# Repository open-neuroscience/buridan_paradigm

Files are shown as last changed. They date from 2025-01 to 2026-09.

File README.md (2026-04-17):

# Buridan paradigm

This project has created open source hardware to perform experiments in a "Buridan paradigm"

First described in 1980 by Goetz [reference](https://pubmed.ncbi.nlm.nih.gov/6779803/) in a visual discrimination context for Drosophila melanogaster, the Buridan Paradigm follows from "buridan's ass" where a hypotetical donkey would die of starvation and thirst if placed at the same distance from a water and a food source, being equally thirsty and hungry. For the experiment using Drosophila, an animal without flying capabilities is placed in an arena, where it is free to walk. Outside of the arena, visual stimuli can be presented, and the movement of the animal towards, or away from these stimuli are recorded and measured.

This implementation of this paradigm relies on commercially available RGB LED Matrices (64x64 leds, with 3mm pitch) and the excellent control library https://github.com/hzeller/rpi-rgb-led-matrix. The system is controlled by a raspberry pi, and it is mechanically put together with Makerbeams, 3D printed parts, screws and nuts. An USB ELP Camera records the fly movement from above. Software was developed in collaboration with [BFKLAB](https://www.bfklab.com/)

Currently (Jan 2026) the system is being tested in the laboratory of [Prof. Sugie](https://www.bri.niigata-u.ac.jp/~neuroscience_disease_sugie/lab/en/) at the Niigata University in Japan 

Researchers and enthusiasts interested in replicating the system can get in touch with [Andre](andremchagas@proton.me)

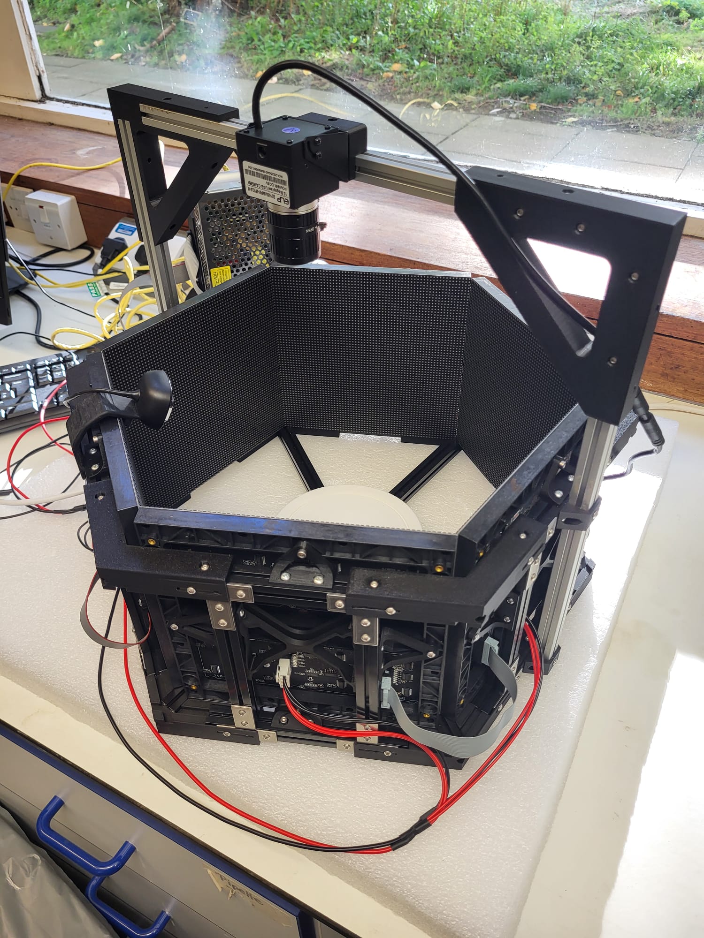
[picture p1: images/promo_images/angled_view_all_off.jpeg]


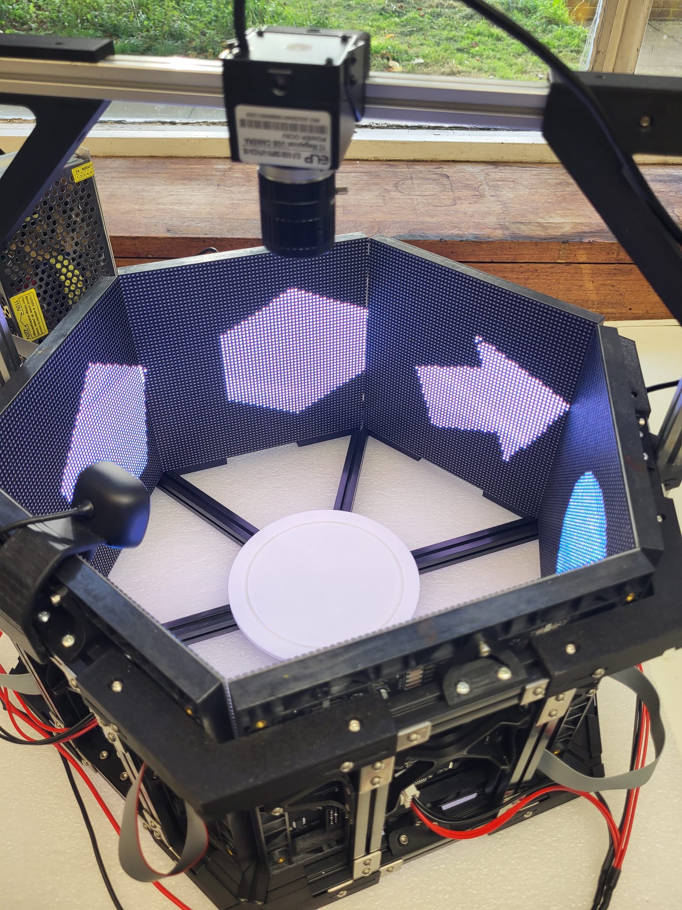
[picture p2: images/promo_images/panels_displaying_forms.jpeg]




---

### Academic references

- https://pubmed.ncbi.nlm.nih.gov/6779803/ - Visual Guidance in Drosophila

### Related hardware components, software, etc

#### LED panels:

- https://elifesciences.org/articles/63355
- https://www.sciencedirect.com/science/article/pii/S096098220800167X
- https://reiserlab.github.io/Modular-LED-Display/

#### Webcams:

- ELP non-IR (high frame rate - up to 250): https://www.amazon.co.uk/ELP-5-50mm-Computer-Comference-Raspberry/dp/B08Y5SG1BF/
- ELP IR: (frame rate up to 60): https://www.amazon.co.uk/ELP-KL36IR-Webcam-Infrared-Camera/dp/B07G56VVYR

#### supporting frames:

- MakerbeamXL: https://www.makerbeam.com/makerbeamxl/

#### RGB matrix driving systems:

- https://github.com/hzeller/rpi-rgb-led-matrix
- https://learn.lushaylabs.com/led-panel-hub75/

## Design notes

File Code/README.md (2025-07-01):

## Install the library
1. Enable ssh
2. Make sure to update rpi
3. ssh from computer (user@)
4. `git clone https://github.com/hzeller/rpi-rgb-led-matrix/`
5. `cd rpi-rgb-led/`
6. `cd lib/`
7. `make`
8. `cd ..`
9. `make` (root rpi led folder)
## Disable sound snd_bcm2835
1. `cd /etc/modprobe.d`
2. `sudo nano alsa-blacklist.conf`
3. type/ add 'blacklist snd_bcm2835'
4. exit nano (ctrl+X,Y)
5. `sudo reboot`
(As seen [here](https://www.instructables.com/Disable-the-Built-in-Sound-Card-of-Raspberry-Pi/))

## Use the demo
1. `cd rpi-rgb-led-matrix/examples-api-use`
2. `./demo -D 1 runtext.ppm`
3. Ctrl+C to quit
4. `./demo help` to explore what else you can do
5. `sudo ./demo --led-rows=64 --led-cols=64 --led-chain=2 --led-parallel=3 --led-slowdown-gpio=4 --led-pixel-mapper="U-mapper;rotate:90" -D1 runtext.ppm` is a good example of what the closest thing to working
## Using the custom pixel mapper
In an attempt to maximise frame-rate, we wanted to use 3 parallel chains of 2 rather than 1 chain of 6. The custom pixel mapper allows the 3 parallel chains of 2 in the setup to behave as one long continuous banner. See the example at the end of this doc - since the screens are upside-down they still require a 180 degree rotation.
#### Make Files:
1. `nano lib/horizontal_mapper.cc`
2. copy-paste the contents of horizontal_mapper.cc from this repo
3. `nano lib/horizontal_mapper.h`
4. copy-paste the contents of the `horizontal_mapper.h` file in this repo
#### Update Existing Files:
1.  `nano lib/pixel-mapper.cc`
2.  At the top of the file, add the following, after the includes:
	> #include "horizontal_mapper.h" 
3.  Find the `CreateMapperMap()` function
4.  After the lines that say `RegisterPixelMapperInternal(....)`, add the following (BEFORE `return result;`):
	> RegisterPixelMapperInternal(result, new HorizontalMapper());
5.  Save and quit the file
	* For nano, this is Ctrl+X
6. `nano lib/Makefile`
7.  Near the top of the file there is a line(s) that starts: `OBJECTS = file1.o file2.o etc...`
8. Add `horizontal_mapper.o` after the last `.o` string
	* Note that there may be multiple lines, separated by a `\` - this is fine, just add to the end of the last .o line
9. Save and quit the file
#### Remake
1. `cd lib/`
2. `make`
3. `cd ..`
4. `make`
#### Example use in examples-api-use/:
`sudo ./demo --led-rows=64 --led-cols=64 --led-chain=2 --led-parallel=3 --led-slowdown-gpio=4 --led-pixel-mapper="horizontal_mapper;rotate:180" --led-pwm-lsb-nanoseconds=50 --led-pwm-bits=8 -D1 runtext.ppm`
This example does a few things that a user may find useful:
1. Uses the custom pixel mapper with 180 degree rotation
2. Sets the pulse-length to 50 nanoseconds (the minimum value) to help with fps
3. Sets the bit-depth to 8 - decreasing the range of colours available (from 11-bit) but increases frame rate. Minimum value is 1 for very high fps
4. Displays refresh rate

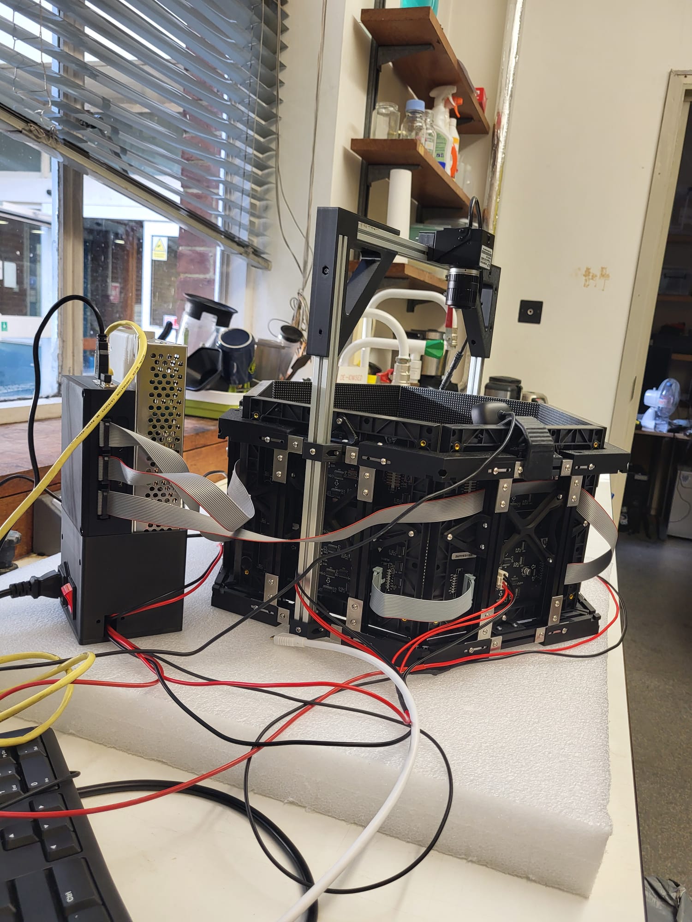
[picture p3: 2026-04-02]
images/promo_images/side_view_with_power_supply.jpeg

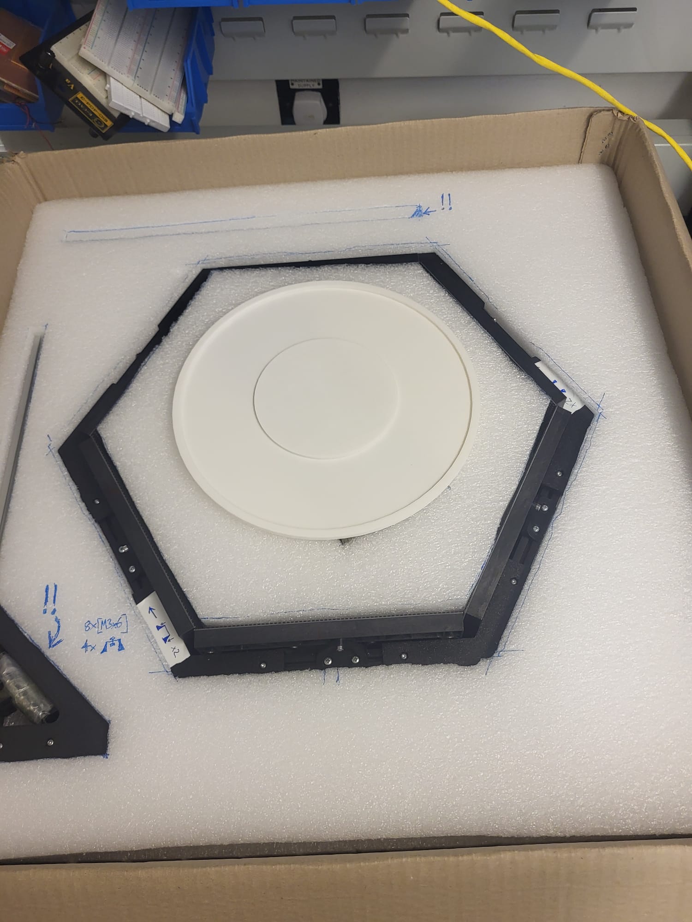
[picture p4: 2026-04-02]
images/promo_images/packaged.jpeg

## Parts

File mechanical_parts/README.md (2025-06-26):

Credit for X-brace design: https://www.printables.com/model/739917-beamcase-x-braces

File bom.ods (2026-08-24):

why | qty | link | unit cost (BRL+shipping) | total cost | obs | cost for parts currently in BRL | total cost
print base where flies will be | 2 | https://www.mercadolivre.com.br/filamento-petg-hf-preto-1kg-impressao-fabricacao-nacional-voolt3d/p/MLB31002299 | 150 | 300 |  | 5946,1 | 7096,1
control visual stimuli | 1 | https://www.mercadolivre.com.br/kit-raspberry-pi4-pi-4-model-b-4gb-ram-novo-nota-fiscal/p/MLB2038781731 | 1200 | 1200 | kit here
power RPI4 | 1 |  |  | 0 | in the kit above
operating system on RPI4 | 1 | https://www.mercadolivre.com.br/cartao-de-memoria-sandisk-ultra-100mbs-32gb-pcameras-wifi/up/MLBU3914236520 | 200 | 200 | in the kit above
connect RPI to computer screen | 1 |  |  | 0 | in the kit above
control raspberry pi for development | 1 | https://www.mercadolivre.com.br/teclado-e-mouse-sem-fio-dell-km3322w/p/MLB23368382 | 170 | 170
connect up to 3 streams of matrices | 1 | https://www.electrodragon.com/product/rgb-matrix-panel-drive-board-for-raspberry-pi-v2/ | 100 | 100
 | 1 | https://www.mercadolivre.com.br/camara-usb-elp-vision-fhd-1080p-angulo-infrarrojo-36-de-/p/MLB2027013675 | 500 | 500
visually stimulation for flies | 6 | https://www.mercadolivre.com.br/modulo-indoor-reposicao-placa-led-p3-64x64-19cm-x-19cm-v10/up/MLBU4214018776 | 250 | 1500
connect matrices to RPI4 | 6 |  |  | 0 | in the bundle above
power everything from one place | 1 | https://www.mercadolivre.com.br/fonte-chaveada-fgb-5v-30a-bivolt-com-protecao-de-curto-circuito/p/MLB38937589 | 120 | 120
 | 1 | https://www.mercadolivre.com.br/conector-painel-de-forca-c14-com-porta-fusivel-10-amperes/up/MLBU1733424013 | 20 | 20
 | 1 | https://www.mercadolivre.com.br/plus-do-brasil-cabo-de-forca-energia-10a-tripolar-p-pc-fonte-computador-cpu-monitor-eletronicos-c13-panela-eletrica-pressao-ro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 | 30 | 30
turn system on/off | 1 | https://www.mercadolivre.com.br/10-botao-liga-desliga-onoff-luminoso-kcd1-106n-escolher-acor/up/MLBU1407091830 | 2,9 | 2,9
hold things in place | 280 | https://www.mercadolivre.com.br/parafuso-cabeca-panela-ph-m3x6mm-zincado-jomarca-100un/p/MLB67849785 | 0,25 | 70
hold things in place | 280 | https://www.mercadolivre.com.br/porca-sextavada-m3-aco-inox-3mm-chave-55--100-pecas/up/MLBU764968165 | 0,19 | 53,2
arena construction | 2 | https://www.makerbeam.com/t-bracket-xl-black-anodised.html | 56 | 112
arena construction | 6 | https://www.makerbeam.com/150mm-4p-black-makerbeamxl-15mmx15mm.html | 50 | 300
arena construction | 2 | https://www.makerbeam.com/200mm-4p-black-makerbeamxl-15mmx15mm.html | 56 | 112
arena construction | 1 | https://www.makerbeam.com/300mm-4p-black-makerbeamxl-15mmx15mm.html | 77 | 77
import tax, shipping, etc | 1 |  | 1079 | 1079
(costs associated with energy, printer maintenance, etc) | 1 |  | 150 | 150
cost associated with building it | 5 |  | 200 | 1000

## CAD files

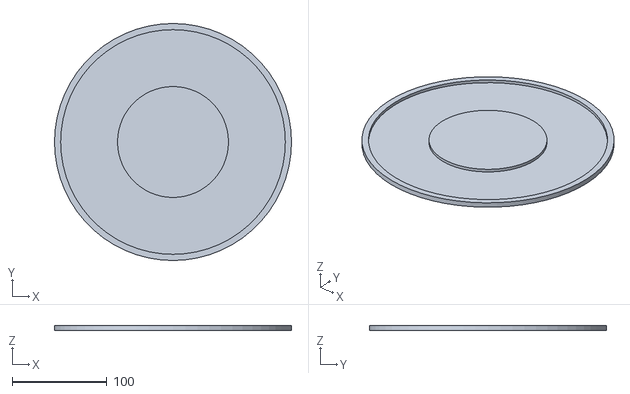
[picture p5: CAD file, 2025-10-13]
mechanical_parts/Arena Assembly 3D Print Parts/fly_base_250.stl
250.0 x 250.0 x 5.00

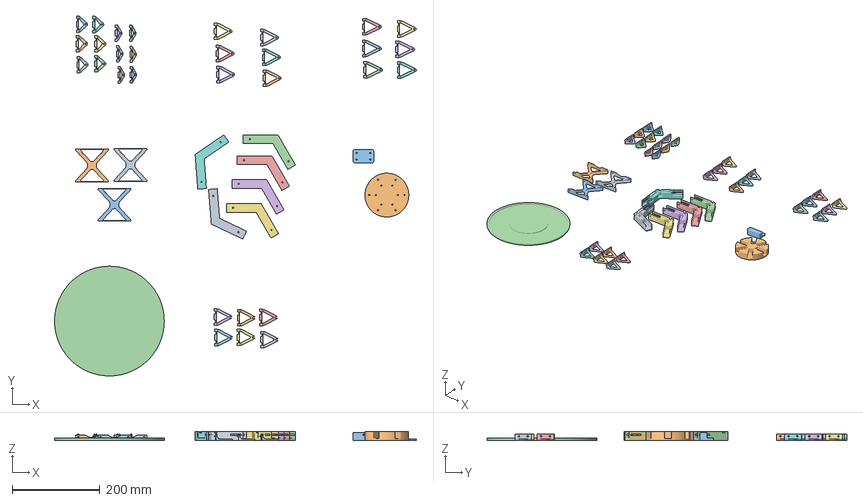
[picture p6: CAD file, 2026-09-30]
mechanical_parts/Electronics Enclosure 3D Print Parts/P1s/P1S_PLA_all_parts_buridan.3mf
824.1 x 819.5 x 20.0 mm
screen bracket_8.stl x 6
screen bracket_17.stl x 6
screen bracket_32.stl x 6
screen bracket_34.stl x 6
Frame X-brace 75x75mm.STL x 3
makerbeam-join.stl x 6
central_join.stl
camera_mount.stl
fly_base_250.stl
test_screen_bracket_32mm.stl x 6

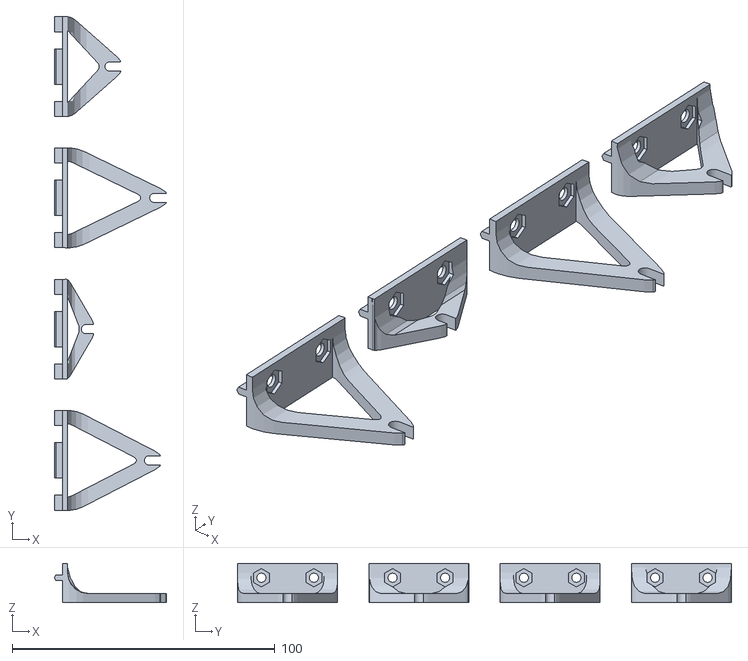
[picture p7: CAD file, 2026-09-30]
mechanical_parts/Electronics Enclosure 3D Print Parts/test_screen_brackets.stl
42.7 x 188.2 x 15.0

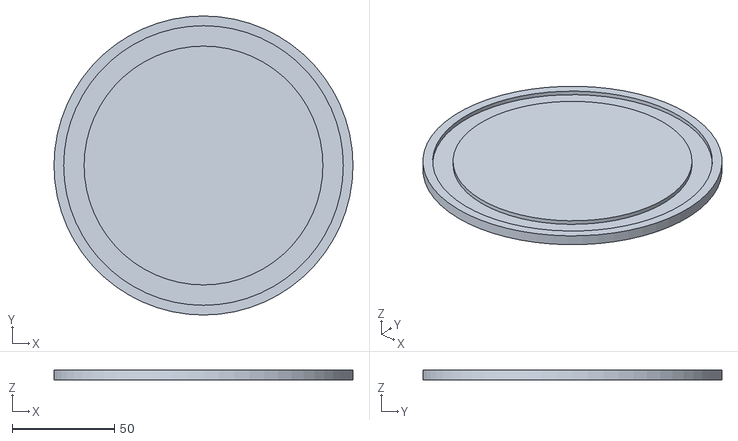
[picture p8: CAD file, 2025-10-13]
mechanical_parts/Arena Assembly 3D Print Parts/fly_base.stl
146.5 x 146.5 x 5.00

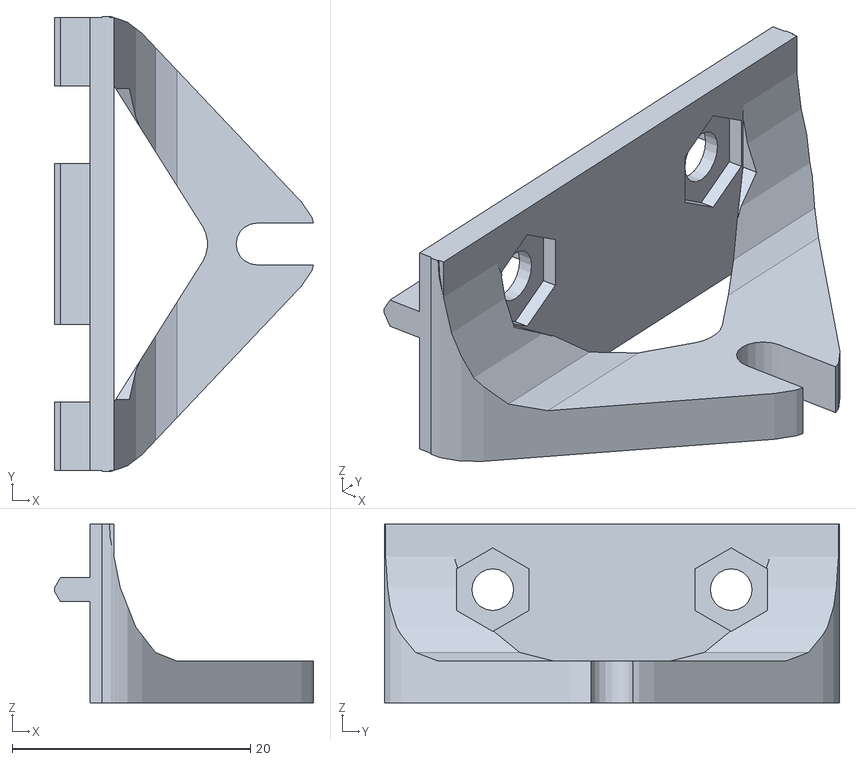
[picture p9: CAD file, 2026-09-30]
mechanical_parts/Electronics Enclosure 3D Print Parts/test_screen_bracket_13mm.stl
21.7 x 38.2 x 15.0

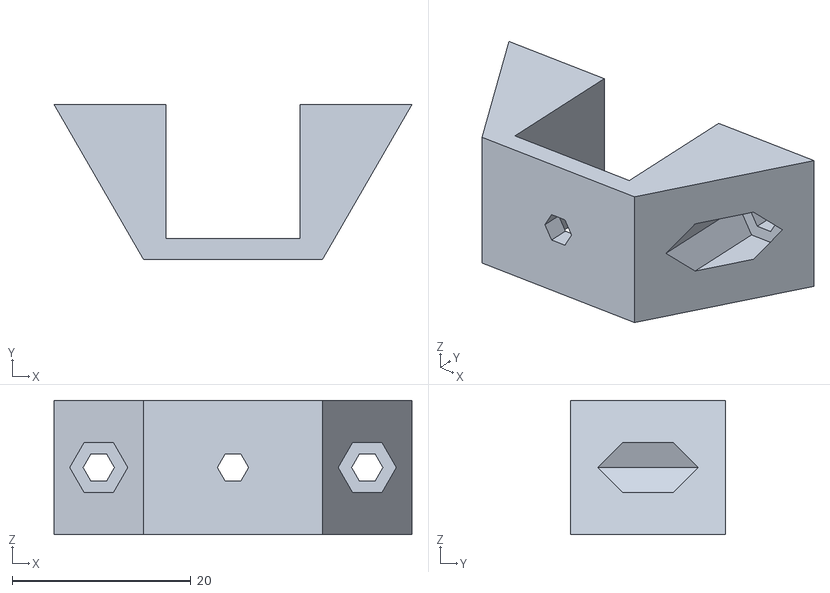
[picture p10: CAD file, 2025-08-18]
mechanical_parts/Arena Assembly 3D Print Parts/vertical beam mount.stl
40.0 x 17.3 x 15.0

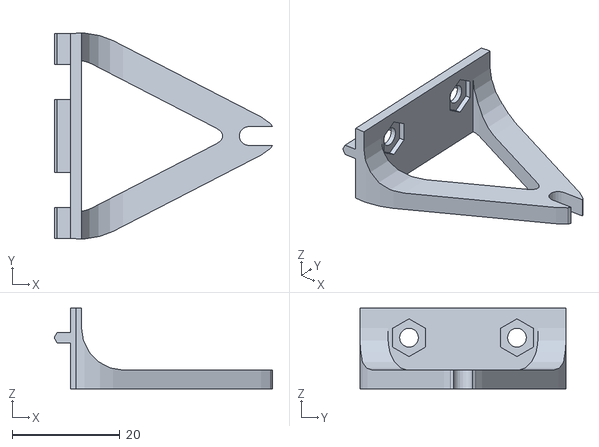
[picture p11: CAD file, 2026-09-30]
mechanical_parts/Electronics Enclosure 3D Print Parts/test_screen_bracket_32mm.stl
40.4 x 38.2 x 15.0

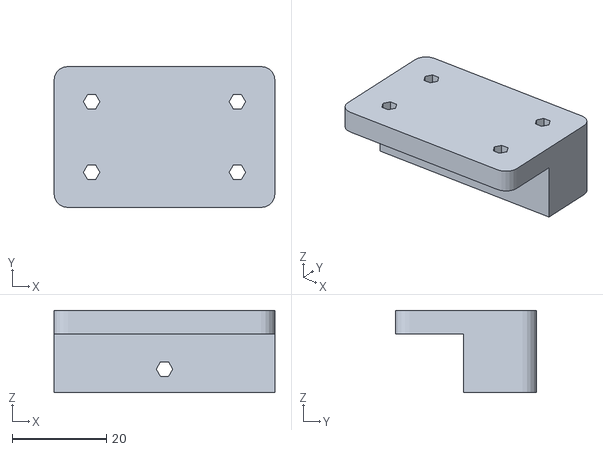
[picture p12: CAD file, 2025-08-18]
mechanical_parts/Arena Assembly 3D Print Parts/camera_mount.stl
47.0 x 30.0 x 17.5

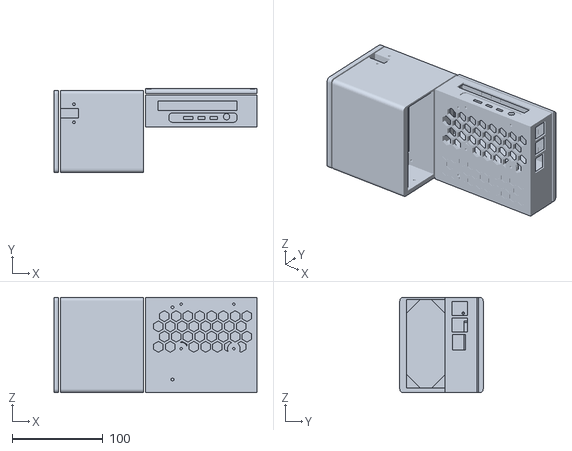
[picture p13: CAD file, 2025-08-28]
mechanical_parts/Electronics Enclosure 3D Print Parts/all_enclosures.stl
223.5 x 92.0 x 105.0

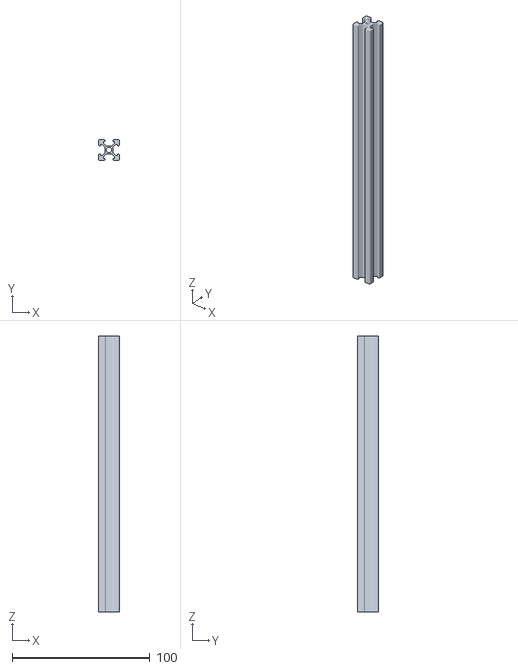
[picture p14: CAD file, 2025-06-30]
mechanical_parts/Arena Assembly 3D Print Parts/makerBeam_200mm.stl
15.0 x 15.0 x 200.0

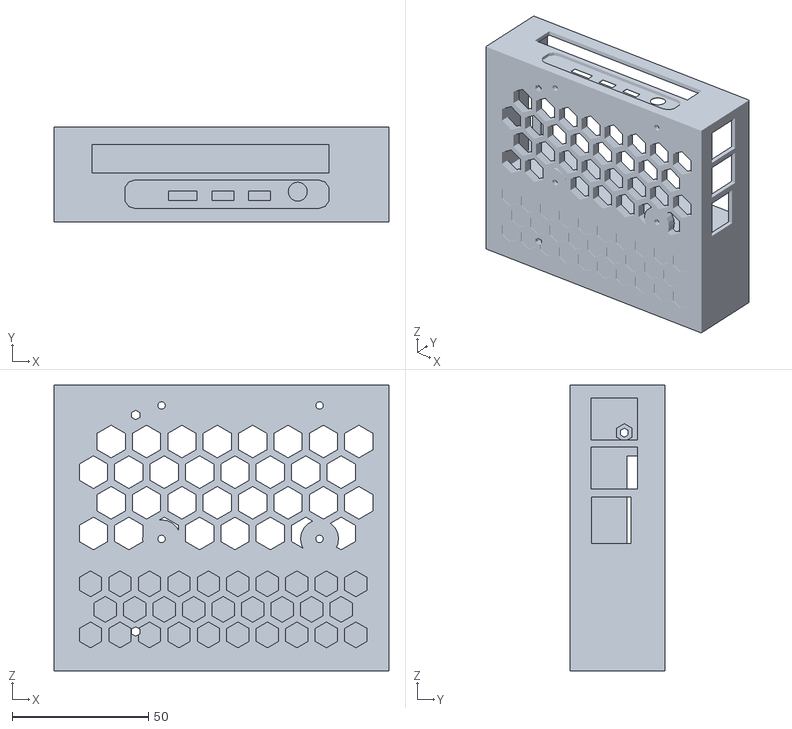
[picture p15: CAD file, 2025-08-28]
mechanical_parts/Electronics Enclosure 3D Print Parts/Enclosure.stl
123.0 x 35.0 x 105.0

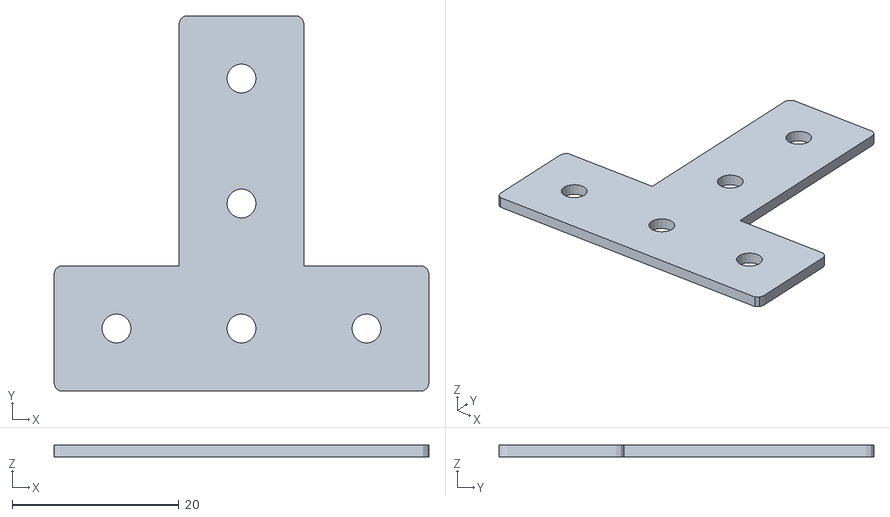
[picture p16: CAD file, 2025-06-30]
mechanical_parts/Arena Assembly 3D Print Parts/makerbeam_t-joint.stl
45.0 x 45.0 x 1.50

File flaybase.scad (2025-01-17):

//Buridan paradigm///
//fly plaform v0.1//
//CC BY SA 4.0 //
// first design by Andre Maia Chagas 17/01/2025//
//units in mm //

platD = 117;
platH = 5;
platEdgeD = 146.5;//platD+8;
tolerance = 0.1;
$fn=60;

//make platform
difference(){
cylinder(d=platEdgeD,h=platH,$fn=60);
translate([0,0,3]){
cylinder(d=platD+5,h=2.5);
}//end translate
}//end difference
cylinder(d=platD,h=platH);
%cylinder(d=platEdgeD+22.8,h=platH,$fn=6);

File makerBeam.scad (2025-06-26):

//Credit: https://www.thingiverse.com/thing:27825/files

$fn=50;

module makerBeam(length)
{
	difference(){
		union(){
			// body
			cube([8,8,length], center=true);
			// corners
			for (i=[0:3]){
				rotate([0, 0, i*90]){corner(length);}
			}
		}
		// center hole
		cylinder(h=length, r=2.5, center=true);
	};
}

module corner(length){
	difference(){
		union(){
			// arm
			rotate([0, 0, 45]){
				translate([0,5,0]){cube([1.4, 15, length], center=true);}
			}

			translate([-9, 7, 0]){cube([2, 6, length], center=true);}
			translate([-7, 9, 0]){cube([6, 2, length], center=true);}
			translate([-7, 7, 0]){cube([3, 3, length], center=true);}
		}

		translate([-4, 10, 0]){cylinder(h=length, r=0.5, center=true);}
		translate([-10, 4, 0]){cylinder(h=length, r=0.5, center=true);}

		// round external shape
		difference(){
			translate([-9.5, 9.5, 0]){cube([1, 1, length], center=true);}
			translate([-9, 9, 0]){cylinder(h=length, r=1, center=true);}
		}
	}
}


makerBeam(50);

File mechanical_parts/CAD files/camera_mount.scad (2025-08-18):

//camera mount

use <fillets_and_rounds.scad>

module camera_mount(){
    x_offset = 15.5;
    y_offset = 7.5;
    
    difference(){
    union(){
        add_rounds(axis="z",R=3,fn=20)cube([47,30,5],center=true);
        translate([0,0,-7.5])add_rounds(axis="z",R=3,fn=20)cube([47,30,15],center=true);
    }//end union
    for(i=[-1:2:1]){
        for(j = [-1:2:1]){
            translate([i*x_offset,j*y_offset,0])cylinder(d=3.5,h=50,center=true);
            //translate([i*x_offset,j*y_offset,-1])cylinder(d=6.5,h=3.5,$fn=6);
        }//end for
    }//end for
}
    
}//end module

module frame_mount(){
    difference(){
    translate([0,8,10])camera_mount();
    cube([60,15,15],center=true);
    rotate([90,0,0])cylinder(d=3.5,h=50,center=true);
        translate([0,15+5.5,0])rotate([90,0,0])cylinder(d=6.6,h=15,$fn=6,center=true);
    }//end difference
}//end frame_mount

frame_mount();

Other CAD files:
mechanical_parts/Electronics Enclosure 3D Print Parts/P1s/PETG_under_support_P1S.gcode.3mf
mechanical_parts/Electronics Enclosure 3D Print Parts/P1s/PETG_arena_structure_brackets_P1S.gcode.3mf
mechanical_parts/Electronics Enclosure 3D Print Parts/P1s/PETG_matrices_structure_brackets_P1S.gcode.3mf
mechanical_parts/Electronics Enclosure 3D Print Parts/P1s/PETG_electronic_enclosures_P1S.gcode.3mf
mechanical_parts/Electronics Enclosure 3D Print Parts/P1s/PETG_fly_arena_P1S.gcode.3mf
mechanical_parts/Electronics Enclosure 3D Print Parts/P1s/PETG_camera_structure_brackets_P1S.gcode.3mf
mechanical_parts/CAD files/Enclosure.scad
mechanical_parts/Arena Assembly 3D Print Parts/Frame X-brace 75x75mm.STL
mechanical_parts/Arena Assembly 3D Print Parts/M3 NUT.stl
mechanical_parts/Arena Assembly 3D Print Parts/M3x6.STL
mechanical_parts/Arena Assembly 3D Print Parts/central_join.stl
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

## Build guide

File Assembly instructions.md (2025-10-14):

## 1. 3D print all parts in this [folder](/mechanical_parts/) to the required part number:  
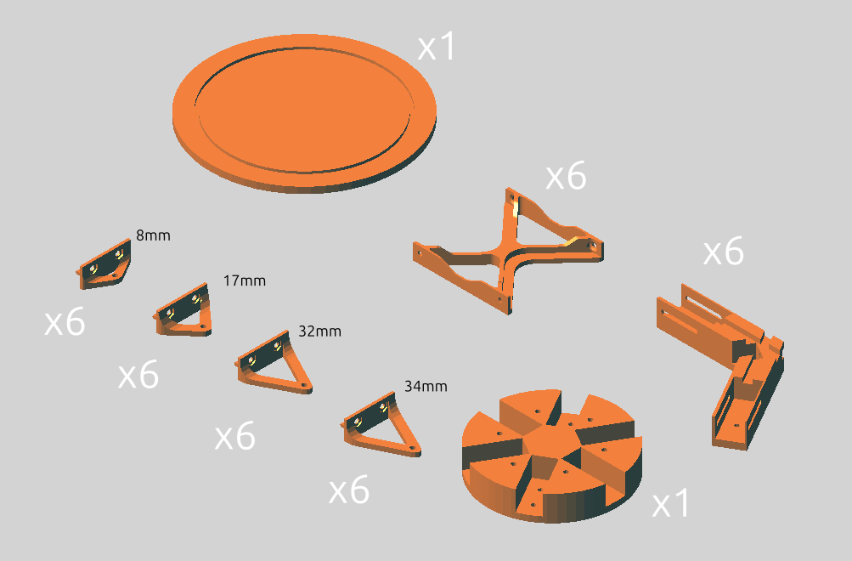
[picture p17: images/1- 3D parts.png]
   
## 2. Assemble 6 screen mounts:
1. Add 4 m3x6 screws and nuts to each (6) X-brace part:  
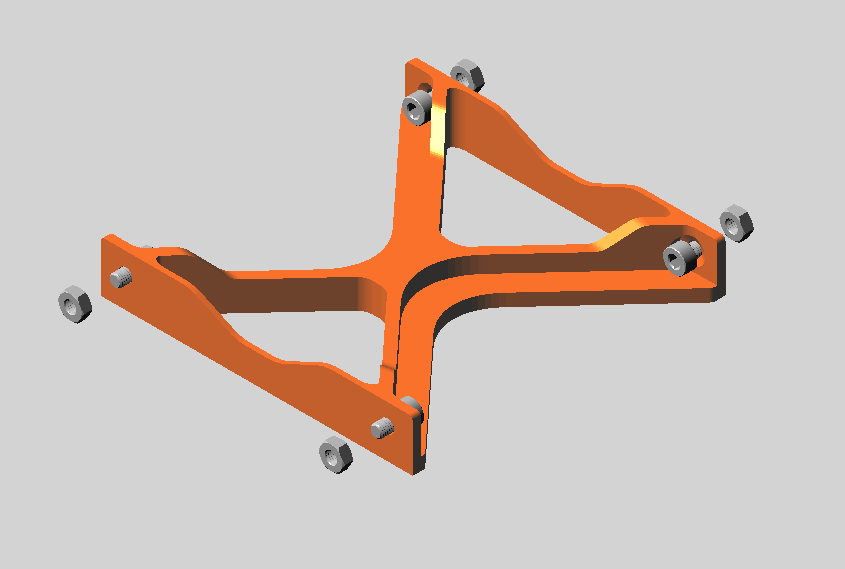
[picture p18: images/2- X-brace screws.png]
   
2. Slide makerbeamXL (150mm) on each side of each X-brace:  
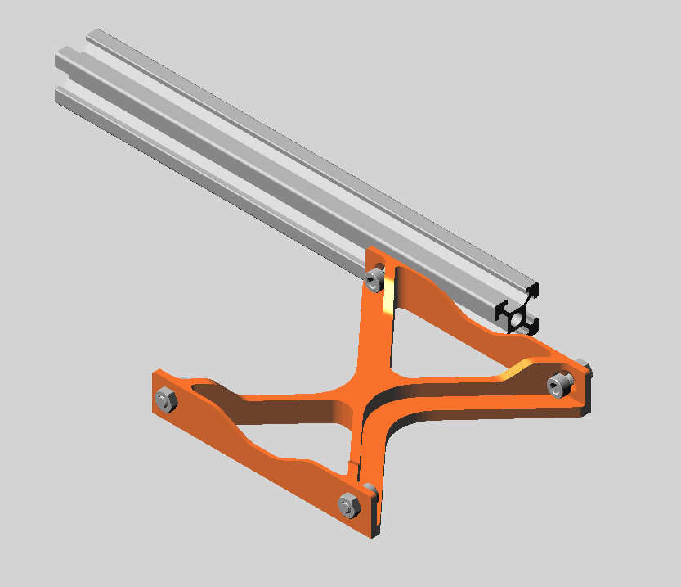
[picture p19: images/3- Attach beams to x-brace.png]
     
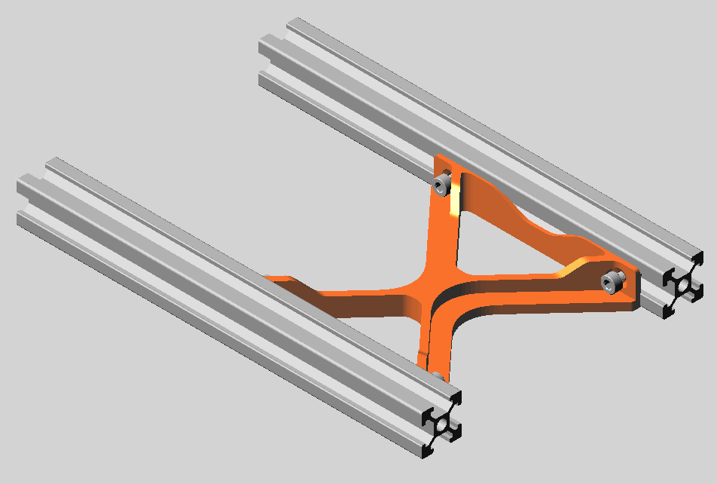
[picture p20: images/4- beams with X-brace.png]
     
3. Slide in 2 nuts to each side and screw on a printed 32mm (image left) and 34mm (image right) screen bracket to each side as shown:  
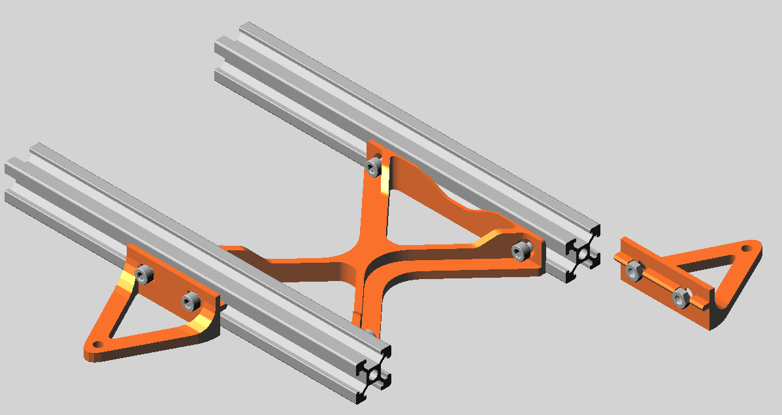
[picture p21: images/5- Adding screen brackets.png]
   
4. Attach screws and nuts to (12) t-plates and insert into the head of each unit as shown: (flipped)  
   _For TWO of these units, make sure to include two extra nuts between the T-plates_
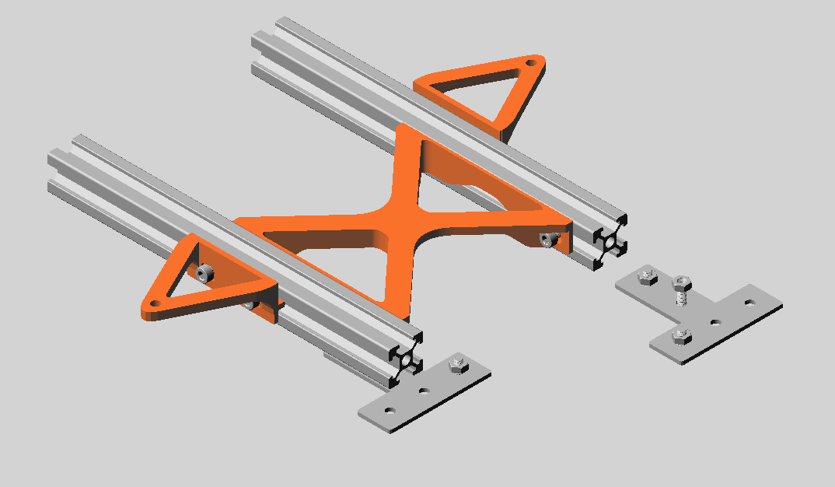
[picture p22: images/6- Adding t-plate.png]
   
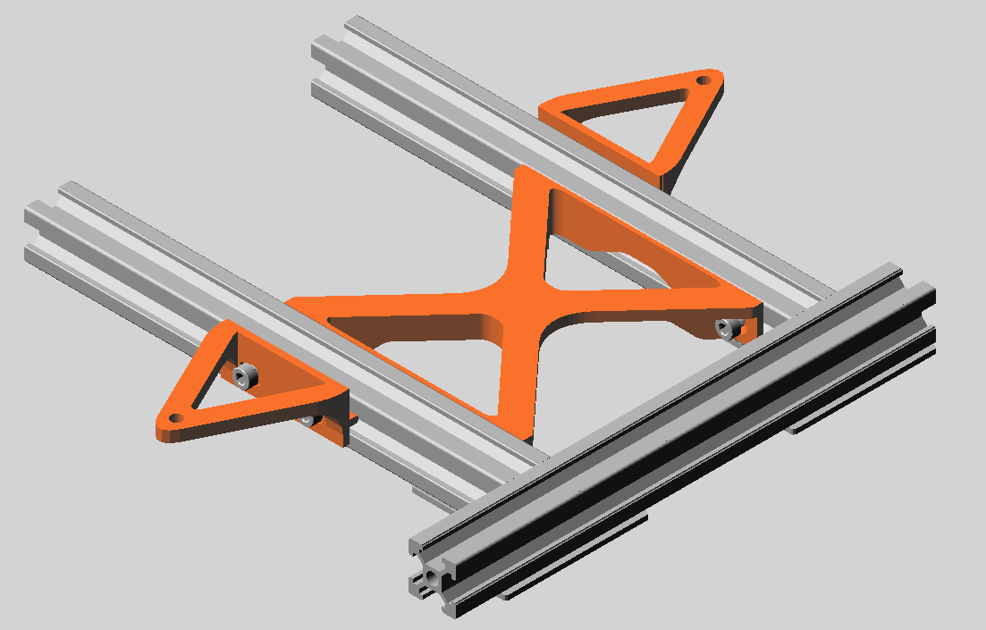
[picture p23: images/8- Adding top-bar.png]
5. Slide another 150mm makerbeamXL on to the top of the unit:    
6. Slide in two nuts and screw on the 17mm screen bracket:  
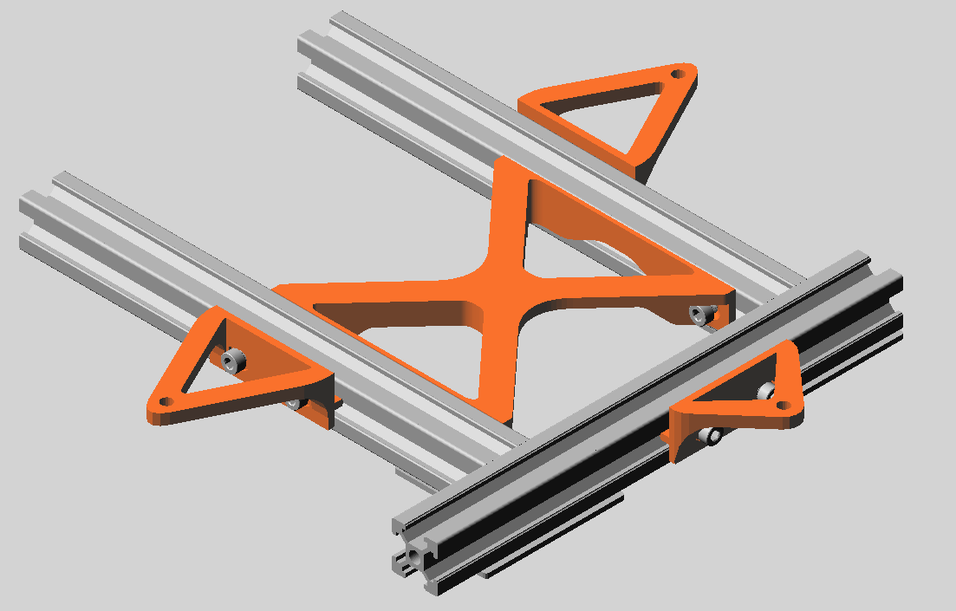
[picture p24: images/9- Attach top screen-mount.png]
     _Remember the extra nuts for two units_  
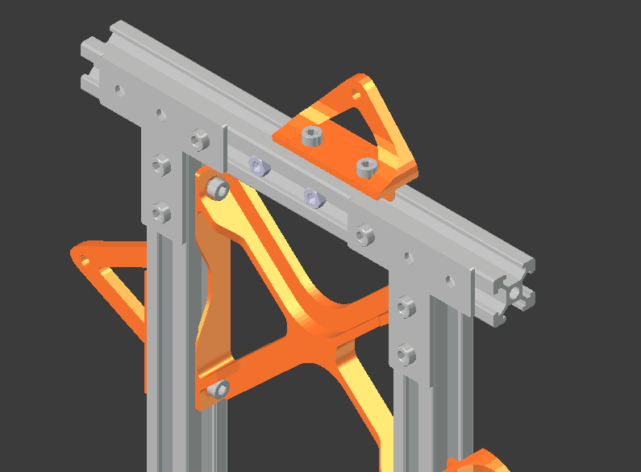
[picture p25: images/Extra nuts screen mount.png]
    
## 3. Assemble central hub
_Remember to glue in magnets to the top holes so they match those in the fly-base_
1. Add screws and nuts to the central hub object:  
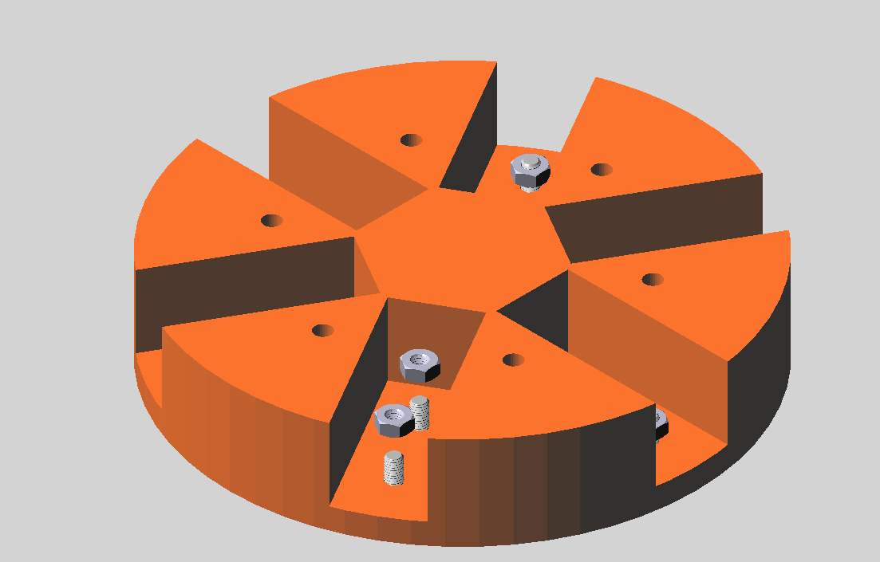
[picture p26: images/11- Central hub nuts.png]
     
2. Slide in six makerbeamXL 200mm beams:
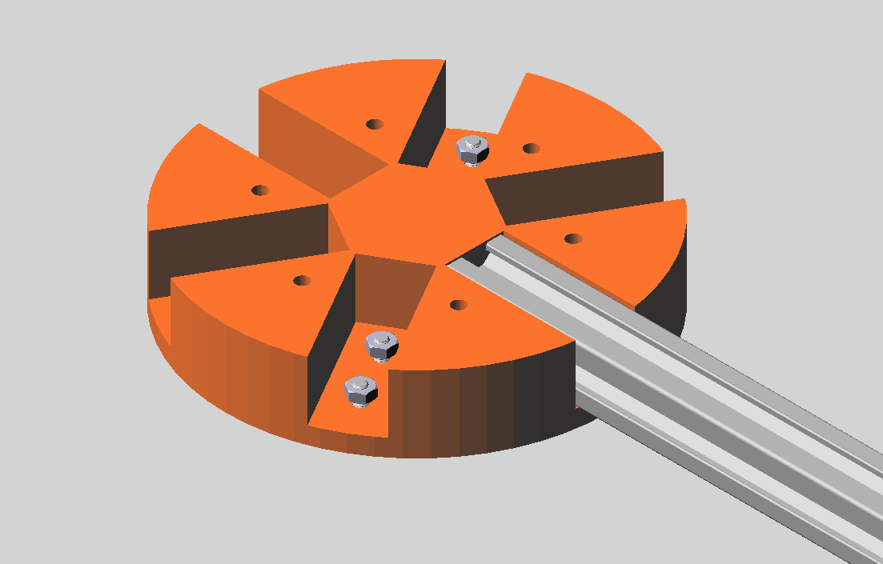
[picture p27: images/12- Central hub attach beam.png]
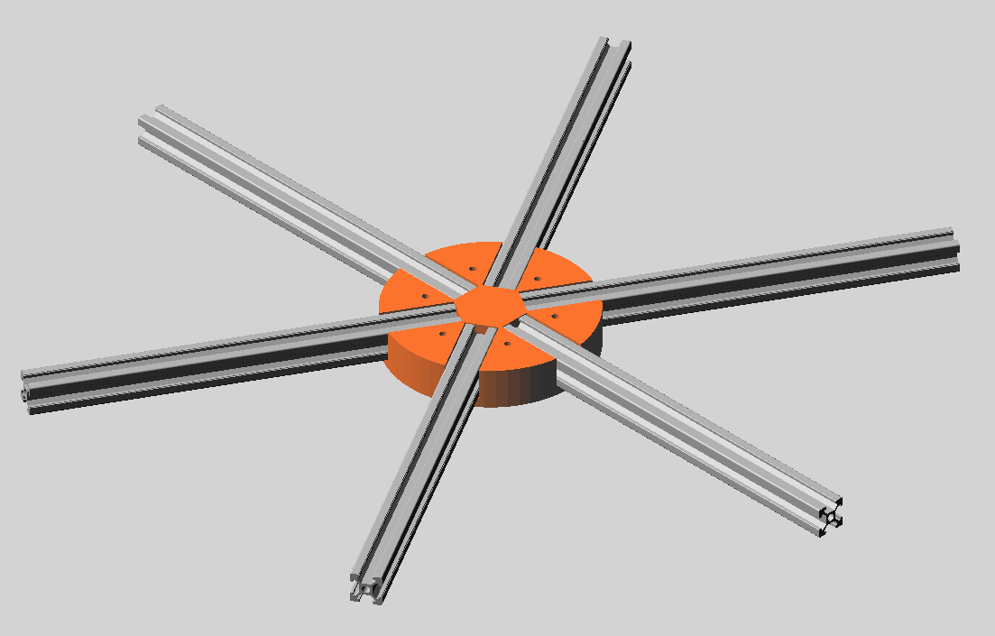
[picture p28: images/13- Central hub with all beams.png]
       
## 4. Assemble the Base
1.  Add screws and nuts to the corner join parts (x6):  
2. Attach a 150mm makerbeam and t-plate (x5): 
	_Don't forget the  nuts shown (left) for two units)
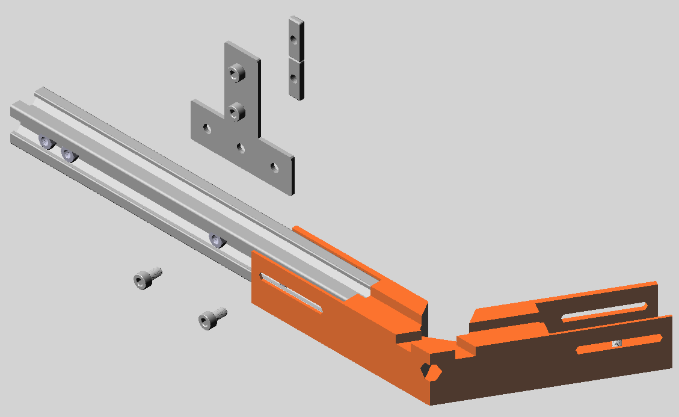
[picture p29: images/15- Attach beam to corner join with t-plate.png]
	
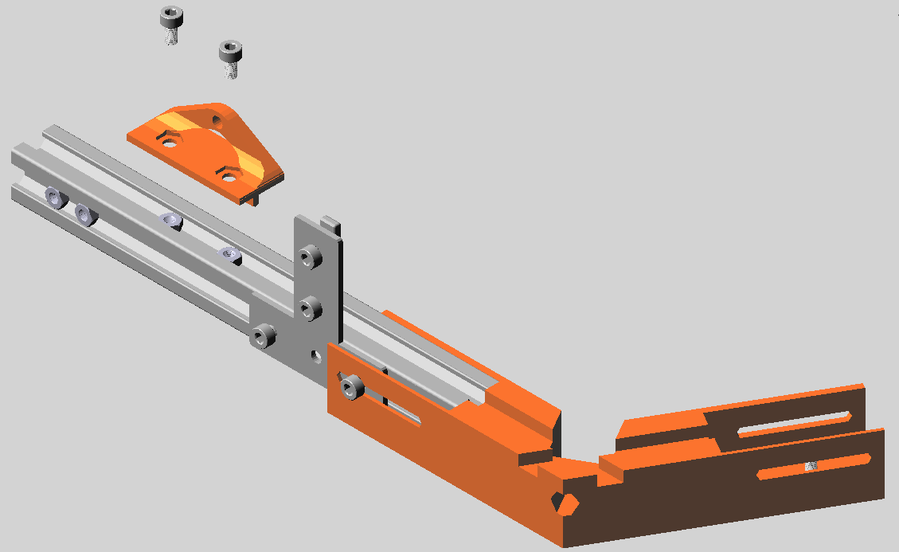
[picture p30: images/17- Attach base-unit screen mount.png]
3.  Add two more nuts to the top of the beam and attach the 8mm screen bracket: 
4.  Insert two extra nuts into TWO sections only:
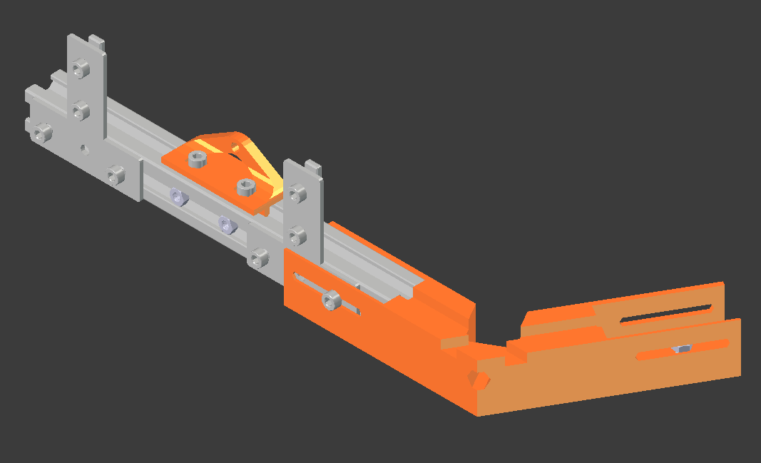
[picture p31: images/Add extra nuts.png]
	
5. Attach the remaining corner part and slot together as shown:
	_Make sure the two sections with extra nuts are OPPOSITE
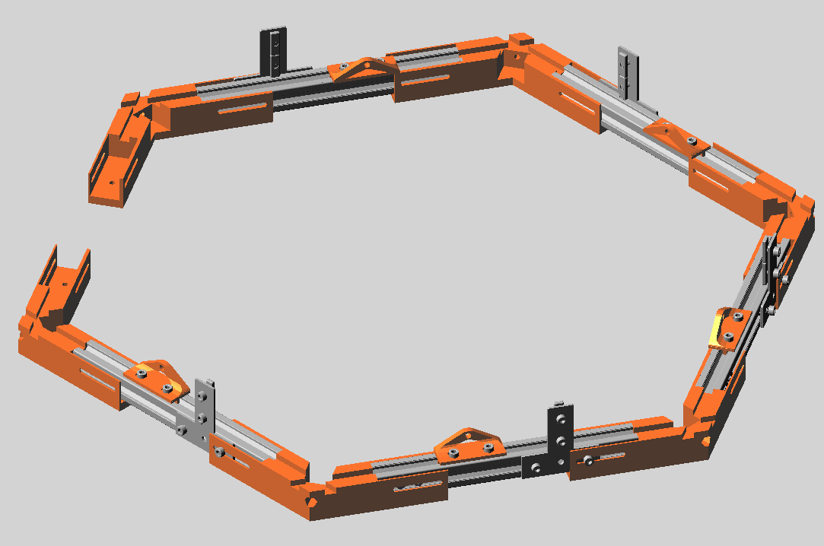
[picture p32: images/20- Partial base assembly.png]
	Note that these parts aren't yet screwed together_  
	
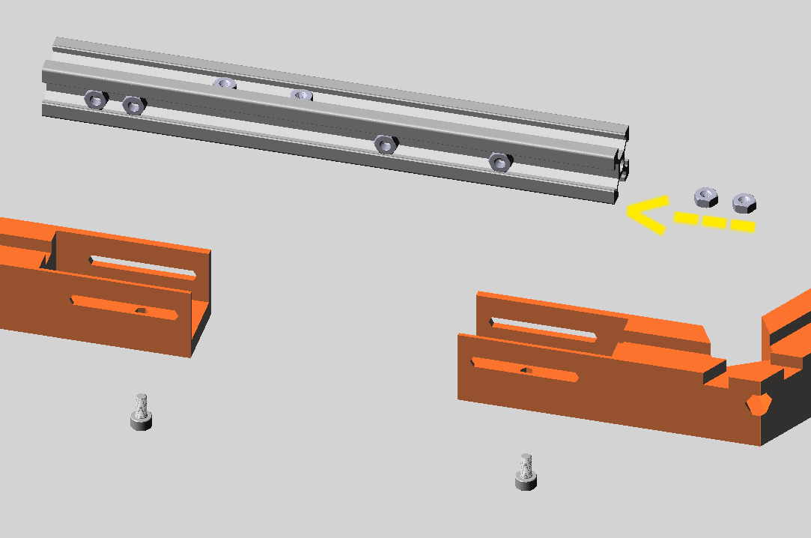
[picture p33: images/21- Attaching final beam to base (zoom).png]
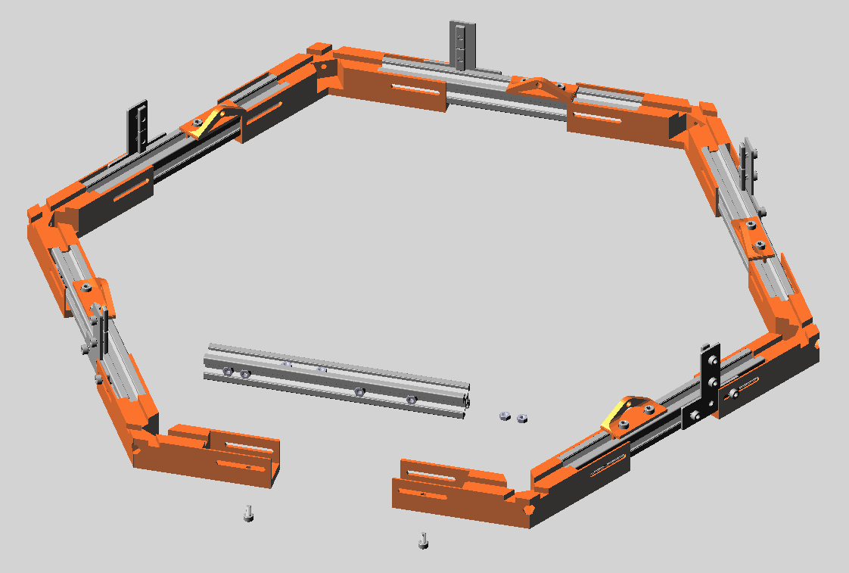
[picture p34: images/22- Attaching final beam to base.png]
6.  Attach the remaining beam with nuts as shown:   
7.  Attach remaining t-plates and screws: 
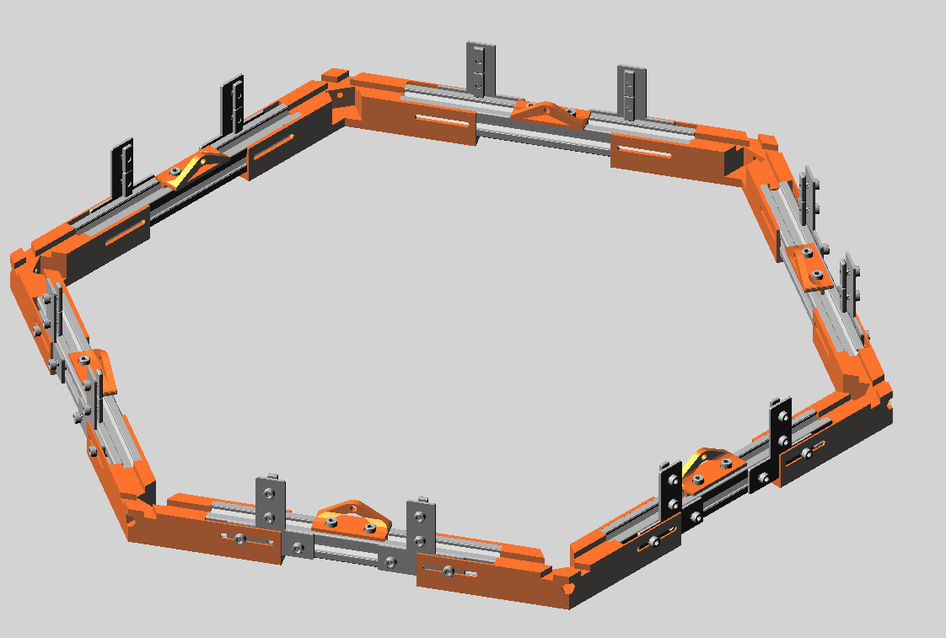
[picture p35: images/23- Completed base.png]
   _Note it's best to keep the screen mounts and t-plates loose enough to slide so they can be adjusted later_
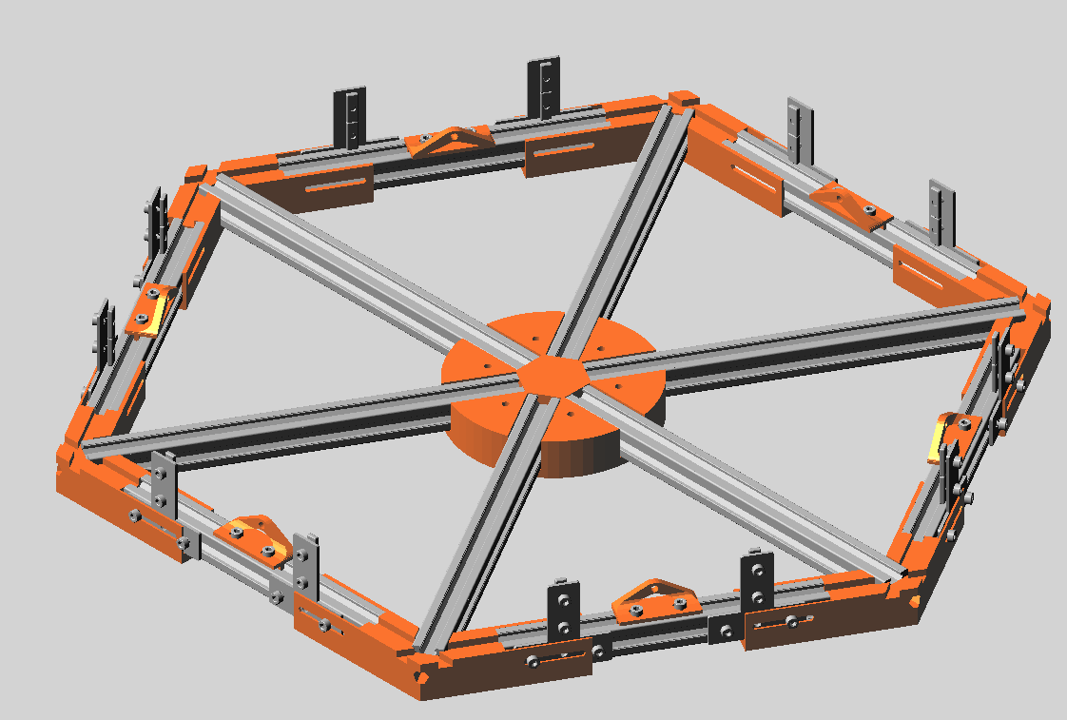
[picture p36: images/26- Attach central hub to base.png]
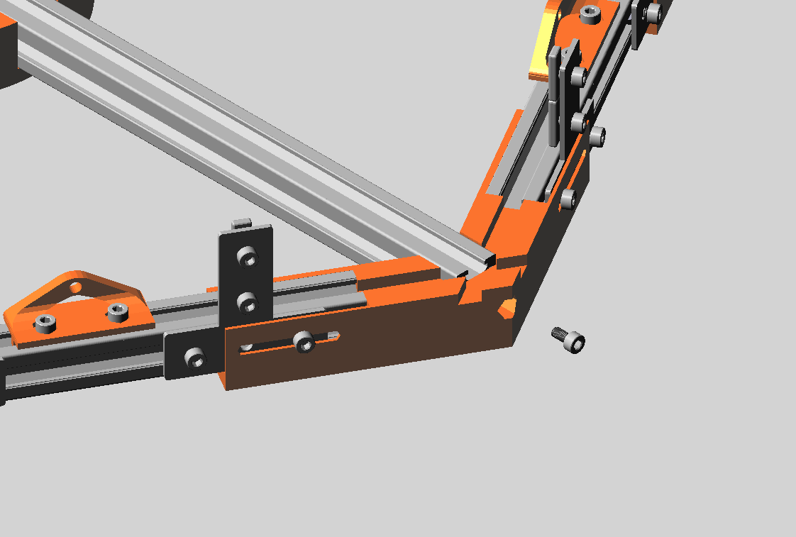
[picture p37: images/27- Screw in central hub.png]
8. Attach the central hub   
## 5. Finish the Frame
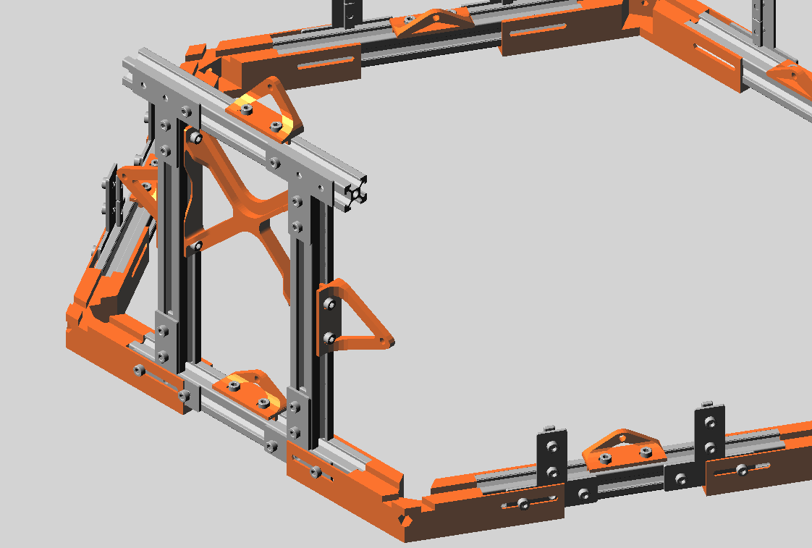
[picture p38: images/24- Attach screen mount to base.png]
1. Attach the screen mounts to the base  (x6)
2. Add nuts to the screen mount and attach the top
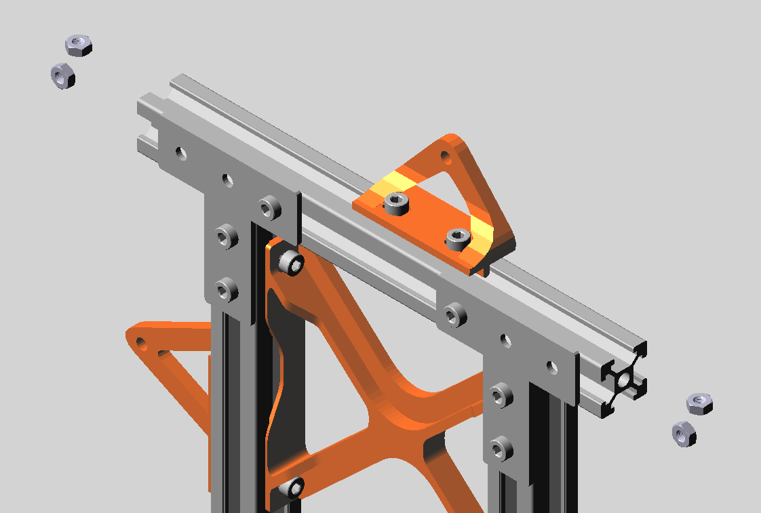
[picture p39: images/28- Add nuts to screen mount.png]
   
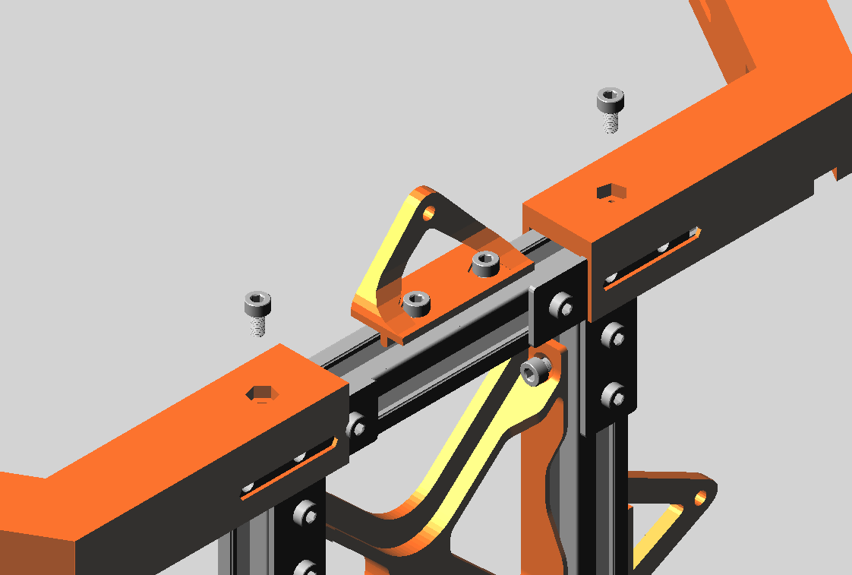
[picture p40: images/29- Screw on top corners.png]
   
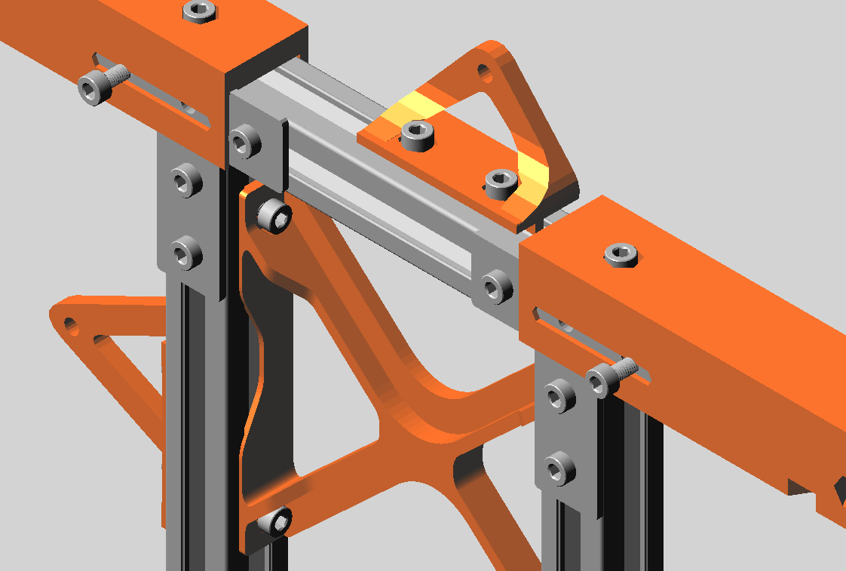
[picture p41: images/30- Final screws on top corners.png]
   
   _Make sure that the top and bottom units with extra nuts are aligned!_
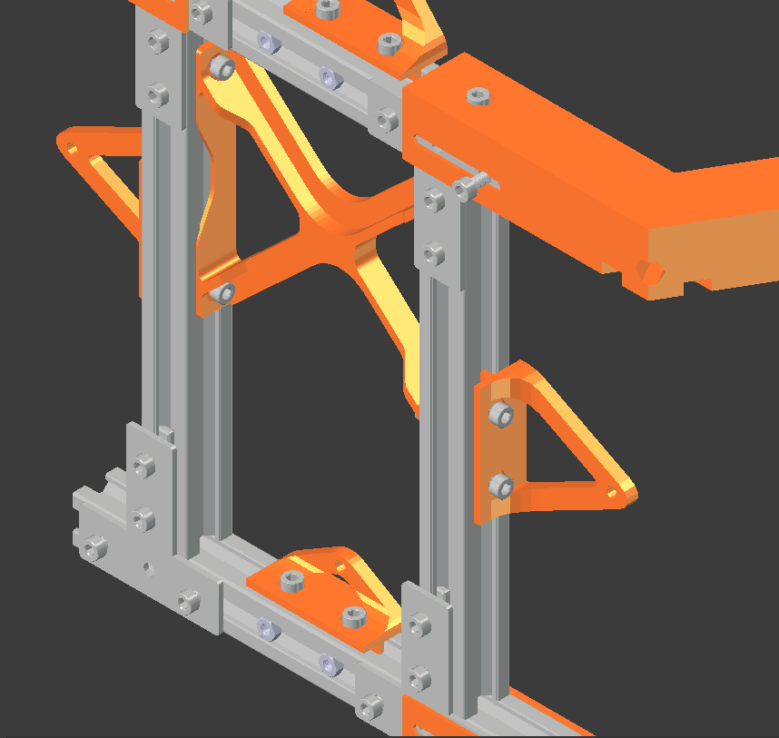
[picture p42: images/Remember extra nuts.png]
   
3. Good job!
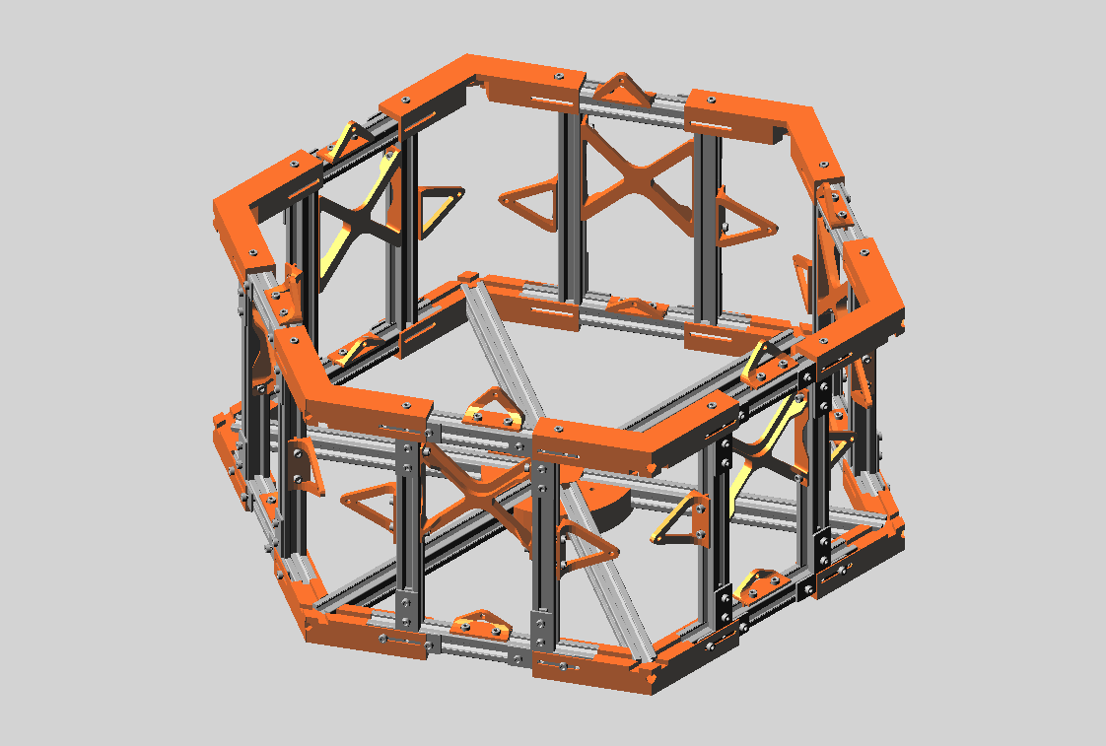
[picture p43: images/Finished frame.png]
   
4. Add nuts to Vertical mounts (x4)  
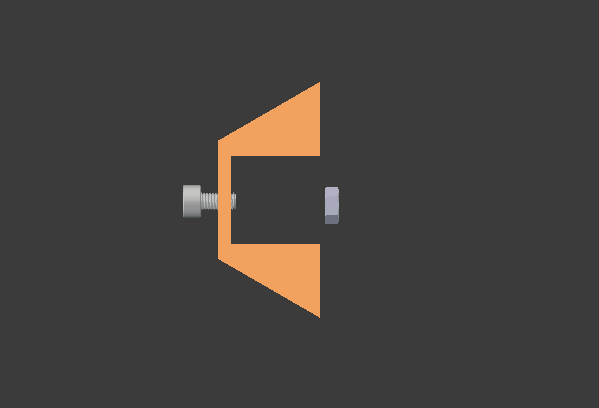
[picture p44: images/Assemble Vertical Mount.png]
     
5. Attach vertical screen brackets to sides with extra nuts  
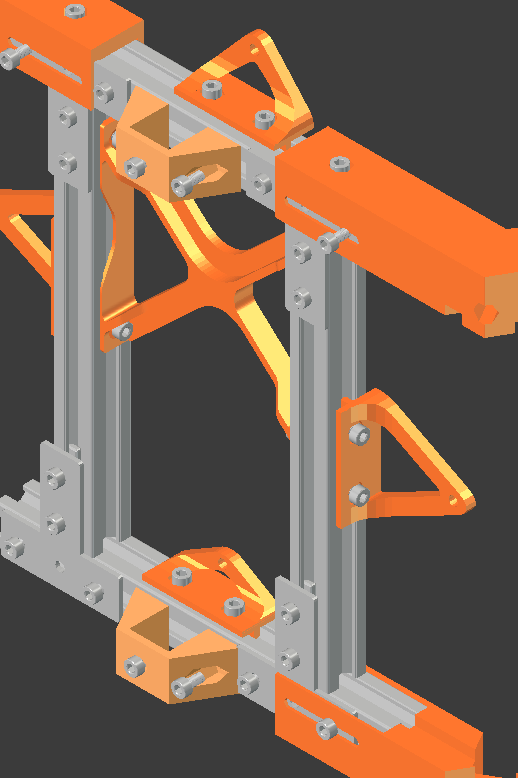
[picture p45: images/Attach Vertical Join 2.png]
   
## 6. Attach the Screens

## 7. Assemble the Camera Mount
1. Attach the Camera to the mount
2. Slide the mount on to a 200mm beam
3. Add screws + straight nuts to the corner bracket (x2)
4. Slide in 200mm beams (x2)
5. Attach the camera-beam between the two beam-bracket assemblies
   _Ensure the beam-bracket assemblies are facing opposite directions_
6. Slide the whole assembly into the vertical mounts

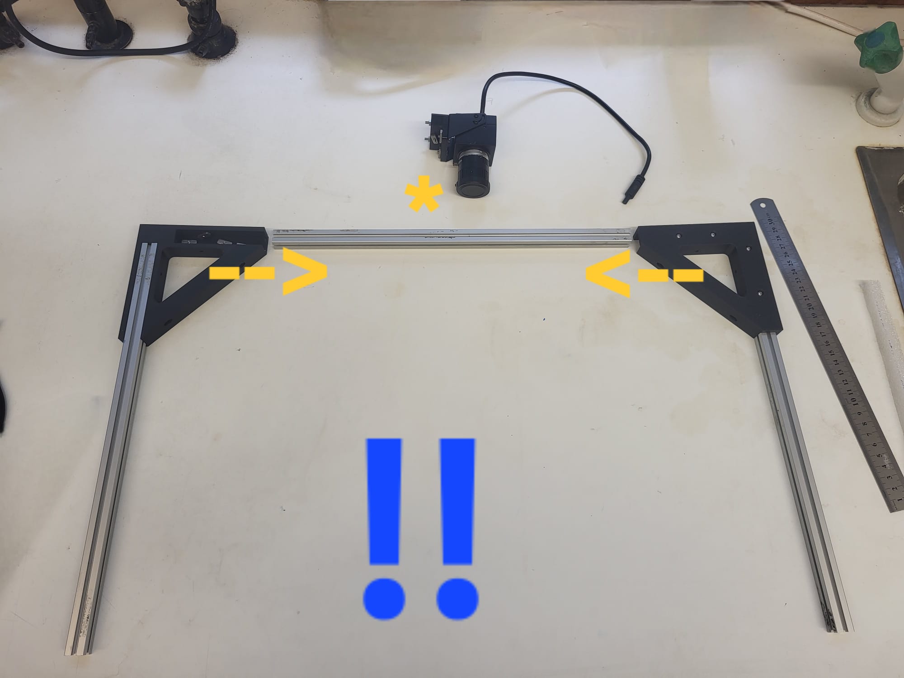
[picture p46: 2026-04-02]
images/promo_images/camera_mount_assembly.jpeg

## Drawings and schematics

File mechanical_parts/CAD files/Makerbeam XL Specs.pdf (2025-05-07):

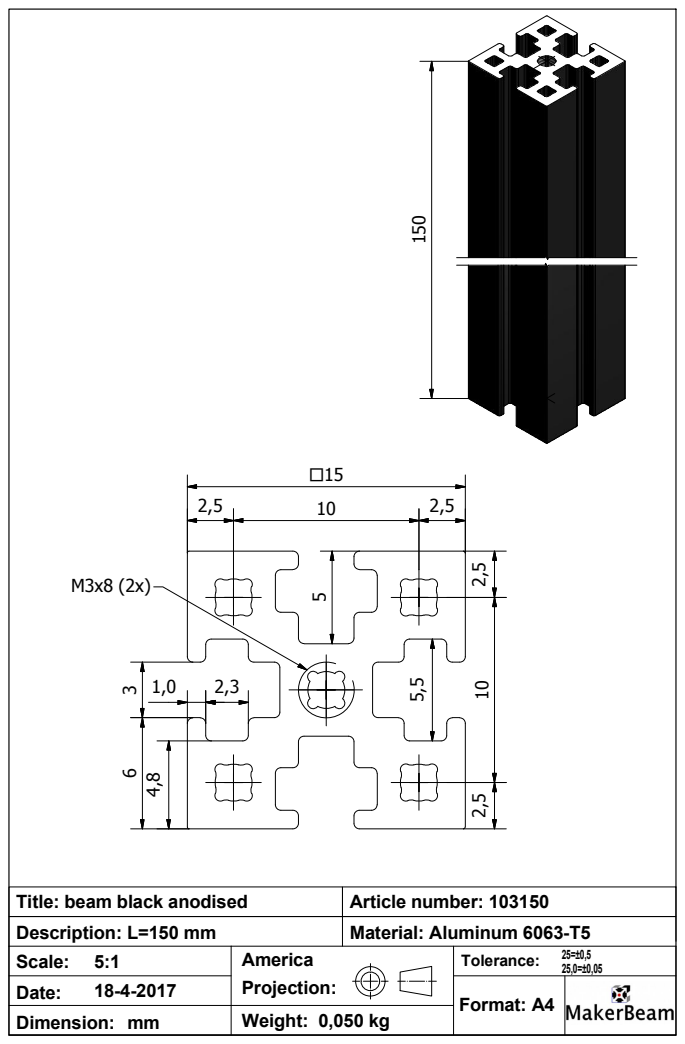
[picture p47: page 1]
America; Weight: 0,050 kg; 25=±0,5 Scale:; Date:; Dimension: mm; Format: A4; Tolerance:; Article number: 103150; Description: L=150 mm; Material: Aluminum 6063-T5; Projection:

Title: beam black anodised

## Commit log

2025-01-17 add a first prototype of the base, and more BOM
    [flaybase.scad, flaybase.stl]
2025-01-18 correct name typos
    [flybase.scad, flybase.stl]
2025-02-20 add simple values for new screen size
    [bom.ods, flybase.scad]
2025-03-01 add more materials and design
    [assembly.FCStd, bom.ods, flybase.scad]
2025-03-03 first bill of materials, plus some design updates
    [bom.ods, flybase.scad]
2025-03-04 add connectors to 3d design
    [flybase.scad]
2025-04-30 update bom and base
    [bom.ods, flybase.scad]
2025-04-30 add more alterantives for the BOM
    [bom.ods]
2025-05-07 organise repo and start making fitting for makerbeam
    [assembly.FCStd, fitting_maker_beam.FCStd, flybase.scad, flybase.stl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]
2025-05-20 Added corner joints
    [assembly.FCStd, flybase.scad, makerbeam-join.scad, makerbeam-join.stl]
2025-05-21 updating designs for center spokes
    center spokes needed for stability
    [makerbeam-join v3.stl, makerbeam-join v4.stl, makerbeam-join.scad, makerbeam-join.stl]
2025-05-23 udpate bom
    [bom.ods]
2025-06-05 Add joints for assembly
    [Frame X-brace 75x75mm.STL, central_join.stl, makerbeam-join.scad]
2025-06-24 Screen brackets
    [screen bracket.scad, screen bracket_17.stl, screen bracket_32.stl, screen bracket_34.stl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]
2025-06-24 added in screen brackets
    [fillets_and_rounds.scad]
2025-06-24 Tidying up
    [maker_beam_fit.stl, makerbeam-join v3.stl, makerbeam-join v4.stl, makerbeam-join.stl]
2025-06-26 Tidying up
    added CAD folder
    [assembly.FCStd, flybase.scad, maker_beam.stp, maker_beam_fit.scad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]
2025-06-26 Added supports for over-arching camera beam structure
    [makerbeam-join_90_deg_fn6.stl, makerbeam_join_90_deg.stl]
2025-06-26 models for documentation
    [makerBeam.scad, makerBeam_150mm.stl, makerBeam_200mm.stl]
2025-06-26 move to cad folder
    [flybase.scad]
2025-06-26 update flybase for magnets
    6 3x2mm magnets can now be used to attach the base to the structure for easy cleaning / modification etc
    [flybase.stl, makerbeam-join.stl]
2025-06-30 Added images
    [M3 NUT.stl, M3x6.STL, makerBeam.scad, makerBeam_150mm.stl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]
2025-08-18 Camera mount
    [camera_mount.scad, camera_mount.stl]
2025-08-18 Vertical beam mounts
    for holding the structure to support the camera
    [vertical beam mount.scad, vertical beam mount.stl]
2025-08-18 Electronics enclosure
    3D printable case for rpi and adafruit hat.
    Attaching to PSU to follow
    [Enclosure.scad, Enclosure.stl]
2025-08-21 magnet holes in fly-base
    [fly_base.stl]
2025-08-21 Updated power/electronics enclosures
    [Enclosure.scad, Enclosure.stl, all_enclosures.stl, hex_grid.scad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]
2025-08-21 Create Subfolders for models
    [Enclosure.stl, Frame X-brace 75x75mm.STL, M3 NUT.stl, M3x6.STL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]
2025-08-22 Updated models
    [Enclosure.scad, Enclosure.stl, all_enclosures.stl]
2025-08-28 small fixes to enclosure
    [Enclosure.scad, Enclosure.stl, all_enclosures.stl]
2025-10-13 Upscaled flybase water moat
    [fly_base.stl, fly_base_250.stl, flybase.scad, flybase0.scad]
2025-10-14 Assembly documentation
2025-10-14 Update Assembly instructions.md
2025-10-14 Update 21- Attaching final beam to base (zoom).png
